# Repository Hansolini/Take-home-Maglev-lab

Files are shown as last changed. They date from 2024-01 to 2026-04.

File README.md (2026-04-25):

# Take-home Maglev lab \:magnet\:

<table align="center">
  <tr>
    <td align="center">
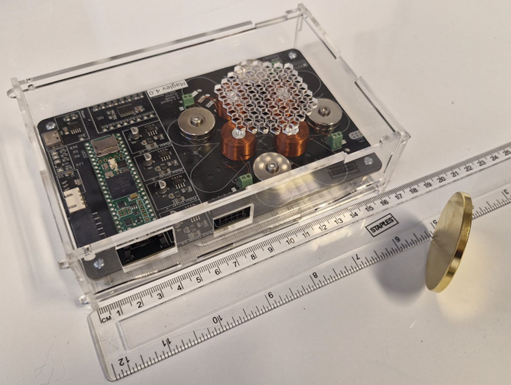
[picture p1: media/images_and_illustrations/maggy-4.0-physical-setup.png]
current hardware
      <br>
      1) Current version of the hardware.
    </td>
    <td align="center">
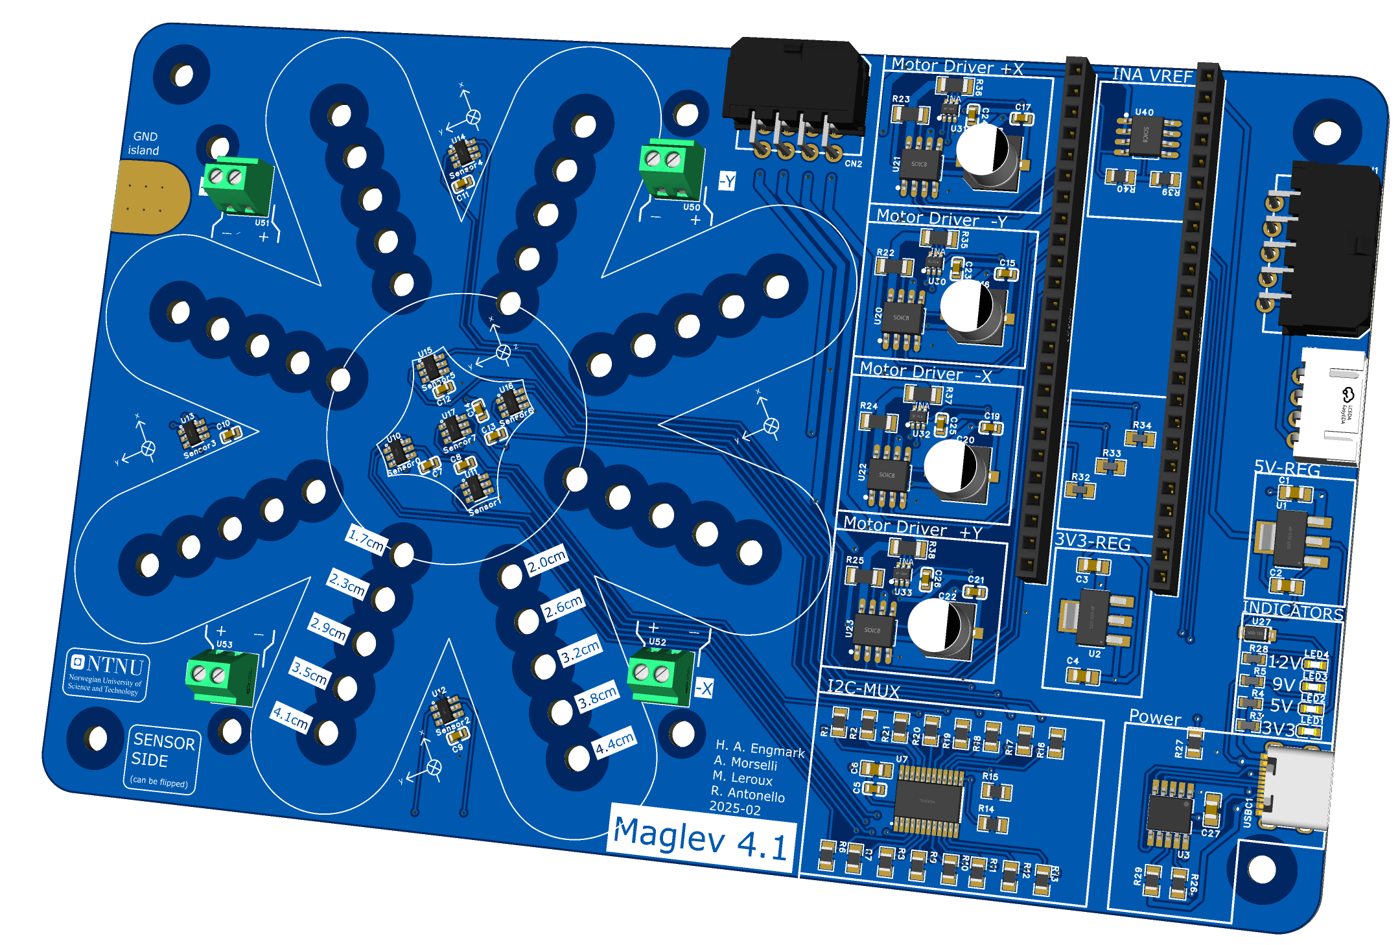
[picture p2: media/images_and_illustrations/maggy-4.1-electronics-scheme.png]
current electronics
      <br>
      2) Overview of the current PCB.
    </td>
    <td align="center">
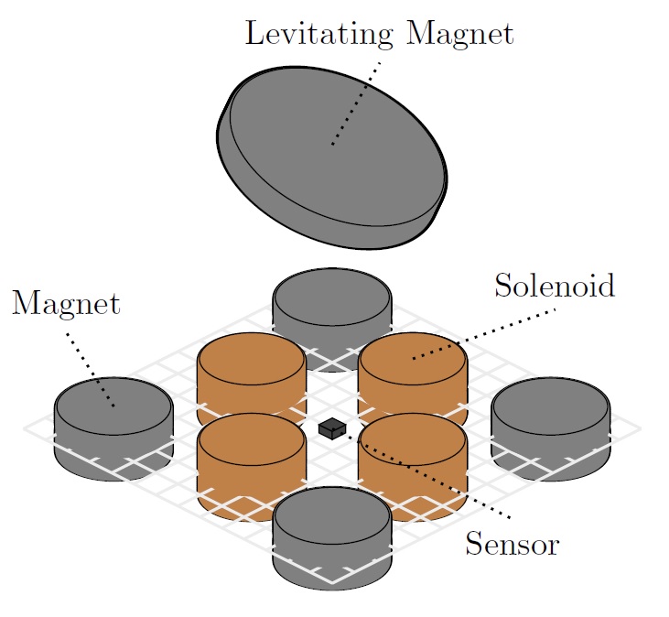
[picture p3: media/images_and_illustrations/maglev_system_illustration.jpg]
magnetic structure
      <br>
      2) Magnetic structure of the system.
    </td>
  </tr>
</table>

The "Take-home Maglev lab" is a small lab in development at the Norwegian University of Science and Technology (NTNU), University of Padova, Italy, and University in Stavanger, Norway. The setup is tailored to help students learn control and related fields, and is intended as a kit that students can bring home and assemble independently, with additional lab assignments for teaching anything from fundamental to advanced concepts within control engineering.

If you want to see how the platform looks like and how effective it is to achieve levitation (actually with a PD controller in this case), see [this](https://youtube.com/shorts/XnbO15yq0vE) and [this](https://youtube.com/shorts/F0SiuVEP2tM) videos.

As for this repository, it contains a
- **[MATLAB simulator](./simulation),** implementing several models with examples. See [main.mlx](./simulation/main.mlx) for a guide on how to use it.
- **[Design files & software](./physical_system),** and thus PCB files, test code, with examples for how to use the physical system.
- **[Student contributions](./student_contributions),** i.e., theses and project reports from the students that have contributed to the project.

The following is a table about such student reports, summarizing also the hardware development history.
## Project reports \:books\:
### 2022
 1. [M. Brønstad, J. O. Deila, J. Dyerskog, and M. Langklopp, "Magnetic levitation system: Design, prototyping and testing of a digital PID-controller", B.S. thesis, ITK, NTNU, Trondheim, 2022.](./student_contributions/literature/2022_NTNU_bachelor_thesis_MJJM.pdf)
 2. [A. Morselli, "Re-design of a magnetic levitation platform: from an early prototype to a working system", B.S. thesis, DDD, UNIPD, Padova, 2022.](./student_contributions/literature/2022_UNIPD_bachelor_thesis_alberto_morselli.pdf)
 3. [A. Nicetto, "State Space Observers and Controllers for a Take-Home Magnetic Levitation System", B.S. thesis, DDD, UNIPD, Padova, 2022.](./student_contributions/literature/2022_UNIPD_bachelor_thesis_andrea_nicetto.pdf)
 4. [F. D. Marchi, "Modeling and Control of a Magnetic Levitation System", B.S. thesis, DDD, UNIPD, Padova, 2022.](./student_contributions/literature/2022_UNIPD_bachelor_thesis_francesco_de_marchi.pdf)
### 2023
1. [H. A. Engmark, K. T. Hoang, "Modeling and Control of a Magnetic Levitation Platform.", presented at the 22nd IFAC World Congress, Yokohama, 2023 pp. 7276-7281. ](./media/literature/maglev_model_description.pdf)
2. [A. Lincetto, "Towards a Pythonic framework for control and analysis of magnetic levitation systems", B.S. thesis, DDD, UNIPD, Padova, 2023.](./student_contributions/literature/2023_UNIPD_bachelor_thesis_alessandro_lincetto.pdf)
3. [G. Piccolin, "considerations on the software and hardware requirements for the implementation of take-home Maglev control labs", B.S. thesis, DDD, UNIPD, Padova, 2023.](./student_contributions/literature/2023_UNIPD_bachelor_thesis_giulio_piccolin.pdf)
4. [S. Graffer, "State estimation of a Maglev system with the Luenberger observer", Project thesis, ITK, NTNU, Trondheim, 2023.](./student_contributions/literature/2023_NTNU_project_thesis_sverre_graffer.pdf)
5. [P. I. D. K. Fosmo, "Control of a magnetic levitation system using feedback linearization", Project thesis, ITK, NTNU, Trondheim, 2023.](./student_contributions/literature/2023_NTNU_project_thesis_pål_fosmo.pdf)
6. [S. A. Senkaya, "A take home portable MagLev lab for learning electronics and control", Project thesis, ITK, NTNU, Trondheim, 2023.](./student_contributions/literature/2023_NTNU_project_thesis_sacit_ali_senkaya.pdf)
### 2024
1. [P. I. D. K. Fosmo, S. A. Senkaya, S. Graffer, H. A. Engmark, D. Varagnolo, "Maggy: Hands-on control learning with a maglev system", M.S. thesis, ITK, NTNU, Trondheim, 2024.](https://ntnuopen.ntnu.no/ntnu-xmlui/handle/11250/3153592)
2. [P. I. D. K. Fosmo, H. A. Engmark, D. Varagnolo, "Maglev Systems for Control Education", Maglev24, Malmö, 2024.](https://bth.diva-portal.org/smash/get/diva2:1918096/FULLTEXT01.pdf)
3. [A. Dal Bello, "Tracking Visual Markers For Maglev Platforms", B.S. thesis, DSMN, UNIVE, Venezia, 2024.](./student_contributions/literature/2024_UNIVE_bachelor_thesis_alessandra_dal_bello.pdf)
4. [G. D'Auria, "Computer based state observers for magnet systems", B.S. thesis, DEI, UNIPD, Padova, 2024.](./student_contributions/literature/2024_UNIPD_bachelor_thesis_giuseppe_d'auria.pdf)
### 2025
1. [Ø. Damsgaard, "Moving horizon state estimation for predictive control of magnetic levitation systems", M.S. thesis, ITK, NTNU, Trondheim, 2025](./student_contributions/literature/2025_MSc_thesis_-_Ørnulf_Damsgaard_-_Moving_horizon_state_estimation_for_predictive_control_of_magnetic_levitation_systems.pdf.pdf)
2. [M. Mjelde, "Robust Model Predictive Control for a Magnetic Levitation System", M.S. thesis, ITK, NTNU, Trondheim, 2025](./student_contributions/literature/2025_MSc_thesis_-_Mikael_Mjelde_-_Robust_Model_Predictive_Control_for_a_Maglev.pdf)
3. [L. Ongaro, "Adapting a maglev system for the ball and beam control", B.S. thesis, University of Padova, 2025](./student_contributions/literature/2025_BSc_thesis_Ongaro_Leonardo_Adapting_a_maglev_system_for_the_ball_and_beam_control.pdf)
4. [M. Palamin, "Comunicazione tra un sistema maglev e dispositivi esterni: implementazione e implicazioni per la didattica sulla Teoria del Controllo", B.S. thesis, University of Padova, 2025](./student_contributions/literature/2025_BSc_thesis_Palamin_Manuel_Comunicazione_tra_un_sistema_maglev_e_dispositivi_esterni.pdf)
5. [T. Chinello, "Bode and Nyquist plots for the analysis and control of a magnetic levitation system", B.S. thesis, University of Padova, 2025](./student_contributions/literature/2025_BSc_thesis_Chinello_Tommaso_Bode_and_Nyquist_plots_for_the_analysis_and_control_of_a_magnetic_levitation_system.pdf)
6. [T. A. Jonsson, "Implementation of a Moving Horizon Estimator Using the Acados Framework", M.S. project, ITK, NTNU, Trondheim, 2025](./student_contributions/literature/2025_Prosjektoppgave_-_Thomas_Aleksander_Jonsson_-_MHE_for_Maggy.pdf)
7. [E. Bruaset, "Acados-based Implementation of Nonlinear MPC for Magnetic Levitation", M.S. project, ITK, NTNU, Trondheim, 2025](./student_contributions/literature/2025_Prosjektoppgave_-_Eivind_Bruaset_-_Acados_for_Maggy.pdf)
8. [L. Edvardsen, "Reinforcement Learning for MagLev Control", M.S. project, ITK, NTNU, Trondheim, 2025](./student_contributions/literature/2025_Prosjektoppgave_-_Linus_Edvardsen_-_RL_for_Maggy.pdf)
9. [M. Jullum Faanes, "CasADi-based Implementation of Nonlinear MPC for Magnetic Levitation", M.S. project, ITK, NTNU, Trondheim, 2025](./student_contributions/literature/2025_Prosjektoppgave_-_Marius_Jullum_Faanes_-_SMPC_for_Maggy.pdf)

## Development history \:rocket\:
| **Version** | **Developer**                                                  | **Goal**                                                      | **Development period** |      **Status**      | **Result**                  |
| ----------- | -------------------------------------------------------------- | ------------------------------------------------------------- | ---------------------- | :------------------: | --------------------------- |
| V1.0        | M. Brønstad <br> J. O. Deila <br> J. Dyrskog <br> M. Langklopp | Levitaion                                                     | Spring 2022            | \:white_check_mark\: | Stable levitation ~ 2 min   |
| V2.0        | M. Brønstad <br> J. O. Deila <br> J. Dyrskog                   | Smaller form factor, more robust                              | Summer 2022            | \:white_check_mark\: | Stable levitation >> 2 min  |
| V2.5        | JH Technical AS                                                | Fix minor bugs, improve heating and components                | Spring 2024            | \:white_check_mark\: | Stable levitation >> 2 min  |
| V2.6        | A. Morselli                                                    | Fix faulty wiring, changing sensors                           | Spring 2024            | \:white_check_mark\: | Stable levitation >> 30 min |
| V2.7        | A. Morselli                                                    | Modular design and testbench for V3.0                         | Spring 2024            | \:white_check_mark\: | Decisions on design         |
| V3.0        | A. Morselli                                                    | Modular redesign for first 'Take-home lab'                    | Summer 2024            | \:white_check_mark\: | Decisions on design         |
| V3.1        | M. Leroux                                                      | Adding USB-C power                                            | Fall 2024              | \:white_check_mark\: | Improved power delivery     |
| V4.0        | M. Leroux                                                      | New form factor and additional sensing for improved stability | Fall 2024              | \:white_check_mark\: | Improved control            |
| V4.1        | R. Antonello                                                   | Rerouting PCB tracks and updating components                  | Spring 2025            | \:white_check_mark\: | Meets IPC standards         |
| V4.2        | K. Blom                                                        | Creating a MISO version of the board                          | Spring 2025            | \:white_check_mark\: | MISO board                  |
| V4.3        | A. Morselli                                                    | Improving EM compatibility via some rerouting                 | Fall 2025              | \:white_check_mark\: | Improved EM compatibility   |

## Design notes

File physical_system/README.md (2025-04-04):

 Here you find:
- **Hardware:** Blueprints for circuit designs of every version of Maggy, components lists and vector files for protective covers/boxes, as well as test-code for checking if the assembeled hardware works as expected.
- **Software:** Various examples of how to use the different veersions of maggy, e.g., PD control embedded on Teensy, and communication protocols for monitoring and control with a computer.

## Setting up for programming Maggy

Each version of Maggy contains a Teensy 4.1 microcontoller, which handles all of the sensor measuremetns, communication and control. This is easily programmed using the Arduino interface, and most of the scripts above are .ino Arduino. To be able to upload these to the Teensy, the following few steps have to be completed:

1.  Install the latest version of [Arduino IDE](https://www.arduino.cc/en/software).

2. When you launch Arduino IDE, you'll see an empty Arduino sketch. Go to **File >> Preferences** (WINDOWS) or **ARDUINO IDE >> Settings** (MAC), and locate the field labeled **"Additional boards manager URLs"** at the bottom of the window, as shown in Figure 1. Paste the following link into the field:
	- [https://www.pjrc.com/teensy/package_teensy_index.json](https://www.pjrc.com/teensy/package_teensy_index.json)
    Use a comma to separate it if there is already something written in the field.

    <td align="center">
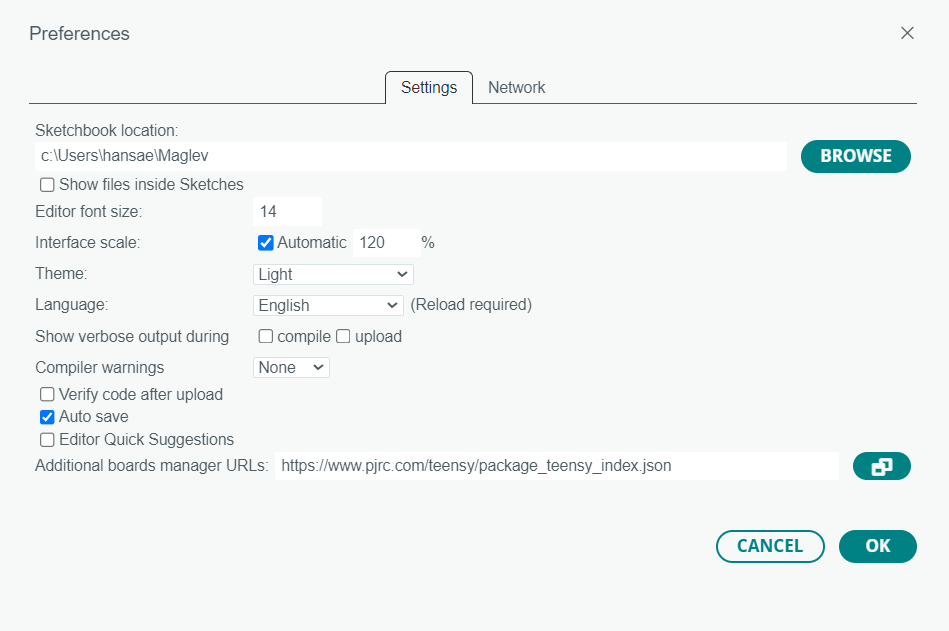
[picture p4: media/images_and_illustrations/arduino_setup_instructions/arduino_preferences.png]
arduino_preferences
      <br>
      Figure 1: Arduino IDE preferences.
    </td>

---

3. Click on **"Boards Manager"** in the toolbar on the left side of the Arduino IDE home screen. Search for "Teensy" and install the Teensy package by Paul Stoffregen, as shown in Figure 2.

	<td align="center">
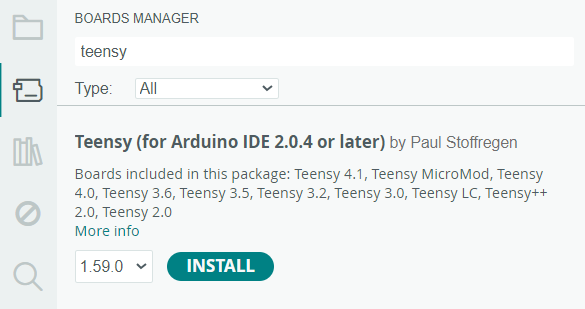
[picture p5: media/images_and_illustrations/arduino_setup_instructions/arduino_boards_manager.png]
arduino_boards_manager
	  <br>
	  Figure 2: Arduino IDE boards manager.
	</td>

---

4. Click on **"Library Manager"** on the left toolbar, search for "TLE493D" (V2x) or "TLV493D" (V4x) in the search field, and install the package from "Infineon Technologies", as shown in Figure 3.

	<td align="center">
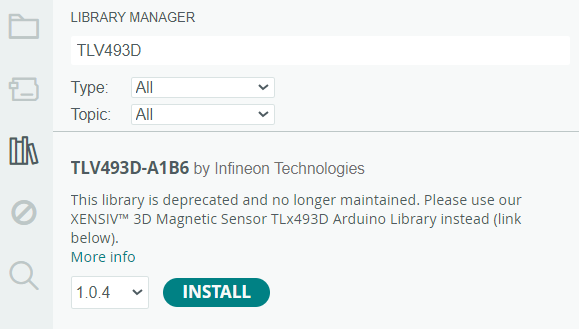
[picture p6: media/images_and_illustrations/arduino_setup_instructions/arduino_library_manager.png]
arduino_library_manager
	  <br>
	  Figure 3: Arduino IDE library manager.
	</td>

---

> **NOTE**: Before powering Maggy, remove the large disk magnet from the system. The scripts we'll run later perform bias-removal routines for measurements, and we don't want to remove the effect of the levitating magnet.

---

5.  Connect Maggy and Teensy to your PC with a micro-USB cable.[1](https://chatgpt.com/c/67e6699f-81f0-8013-9739-4315bfa6288c#user-content-fn-1) Check that you can upload a blank sketch by selecting the COM port of Teensy 4.1 from the **"Select board"** drop-down menu at the top of the window. Click **"Upload"** to compile and upload the sketch to Teensy 4.1. You'll see a lot of red text in the console window during compilation and uploading, but the process is successful if the last lines of text appear as shown in Figure 4.

	<td align="center">
	  teensy_success_message<br>
	  Figure 4: Arduino IDE command window message upon successful compilation.
	</td>
## Footnotes

1. If the Teensy isn't recognized by the PC, connect external power to Maggy by plugging in the power cable on the opposite side of the USB port. [↩](https://chatgpt.com/c/67e6699f-81f0-8013-9739-4315bfa6288c#user-content-fnref-1)

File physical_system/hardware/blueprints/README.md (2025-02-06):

# Blueprints :hammer_and_wrench:
This folder contains information about the hardware for all the different versions of Maggy.

## PCB Designs
The PCB design and production files can be found in each folder. Starting with version 4, it is also possible to view the designs and place orders through EasyEDA. Please refer to the specific folders for more information.

## Other Components
Each version of Maggy uses additional components that must be purchased separately from the PCB files.

### Teensy 4.1
We use the Teensy 4.1 development board, specifically this one:
- [Teensy 4.1 on Elfa Distrelec](https://www.elfadistrelec.no/no/teensy-utviklingskort-med-headers-sparkfun-electronics-dev-16996/p/30216161?ext_cid=shgooaqnono-Shopping-PerformanceMax-CSS&cq_src=google_ads&cq_cmp=20351270785&cq_con=&cq_term=&cq_med=pla&cq_plac=&cq_net=x&cq_pos=&cq_plt=gp&gclid=CjwKCAjw4P6oBhBsEiwAKYVkq0jYkFst_neMMFQlXfZBW9-KxBMFTjGZog-tAYaTsAmTVziUdTWCHRoCGOcQAvD_BwE&gclsrc=aw.ds)
- [Teensy 4.1 on RS Online](https://no.rs-online.com/web/p/microcontroller-development-tools/2836911?cm_mmc=NO-PLA-DS3A-_-google-_-CSS_NO_EN_Pmax_Test-_--_-2836911&matchtype=&&gad_source=1&gclid=CjwKCAiA74G9BhAEEiwA8kNfpfuTP6LMEUCaeJ0THdqRm6JLBaF8OzCmbcy2USRwfd5TNwAT9TSBZxoCiPkQAvD_BwE&gclsrc=aw.ds)

If you want to avoid a lot of soldering, ensure that you order with the headers pre-soldered.

### Electromagnets
The electromagnets are standard 19×12 mm copper coils with around 480 windings. Searching for “19x12 maglev electromagnet” should result in many options. For example:
- [Electromagnet on AliExpress](https://www.aliexpress.com/item/4000076659177.html?spm=a2g0o.productlist.main.1.455ew7Phw7PhcV&algo_pvid=489107c2-cb2e-4235-b999-33f5bcec5149&algo_exp_id=489107c2-cb2e-4235-b999-33f5bcec5149-0&pdp_npi=4%40dis%21EUR%216.78%216.24%21%21%217.18%216.61%21%402103249617062671537431660e604c%2110000015610528766%21sea%21NO%210%21AB&curPageLogUid=W7mtjk8XbjMA&utparam-url=scene%3Asearch%7Cquery_from%3A)
- [Electromagnet on Amazon (US)](https://www.amazon.com/Magnetic-Levitation-Electromagnetic-Induction-Experiment/dp/B0B92X4MB2?th=1)
- [Electromagnet on Amazon (DE)](https://www.amazon.de/-/en/Magnetic-Floating-Electromagnetic-Induction-Experiment/dp/B0B8Z66W5S)

### Permanent Magnets for the Base
For the base, we use neodymium magnets with counterbore holes that are fastened with screws to the PCB. The choice of magnet is flexible, but ensure that the dimensions are similar to the ones listed below. The stronger the magnet, the better (i.e., N40 > N35). Also, all magnets on a single unit should have the same polarity, so it’s advisable to purchase them from the same supplier.

Examples of magnets we have used:
- [20×4 mm Magnet with Mounting Hole (Supermagneter)](https://supermagneter.no//magnet-med-monteringshull-20x4mm-id794)
- [20.0×4.5×4.0 mm Neodymium Ring Magnet (Magnet-Shop)](https://www.magnet-shop.com/neodymium/ringmagnets/ringmagnet-20.0x4.5x4.0-mm-n42-nickel-counterbore-n-pole)

### Disk Magnets
The choice of disk magnets is even more flexible, but the examples below are good options. Thicker and heavier magnets have a higher moment of inertia, which makes them easier to stabilize.
- [50×5 mm Disk Magnet (Supermagneter)](https://supermagneter.no//diskmagnet-50x5mm-id752)
- [50.0×4.0 mm Neodymium Disk Magnet (Magnet-Shop)](https://www.magnet-shop.com/neodymium/discmagnets/discmagnet-50.0-x-4.0-mm-n40-gold-holds-21-kg)

### Misc
Screws, spacers and nuts are all standard 3 mm machine screws that should be available everywhere. If possible, use non-magnetic screws. In particular, we have used these spacers for space between PCB and covers/box:
- [M3 spacer, 15mm, male-female](https://www.digikey.no/no/products/detail/w%C3%BCrth-elektronik/971150354/9488642)
- [M3 spacer, 15mm, female-female](https://www.digikey.no/no/products/detail/w%C3%BCrth-elektronik/970150354/9488567)

Also consider that you might need [USB cables](https://www.digikey.no/no/products/detail/cvilux-usa/DH-20M50057/13177527) for connecting to a computer, some antistatic insulation and cardboard boxes for storage, and laser cut protective plates/boxes for protection (we have used 3 mm acrylic plates, cut with blueprints found in the folders).

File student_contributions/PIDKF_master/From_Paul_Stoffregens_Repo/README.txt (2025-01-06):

This folder contains the code developed by Paul Stoffregen to test Teensy data transmission speed.
I do not claim ownership of any of the code, and credit goes to the original developer.
The original code is located at https://github.com/PaulStoffregen/USB-Serial-Print-Speed-Test/tree/master.

-Pål Ivar Delphin Kværnø Fosmo, June 3rd 2024

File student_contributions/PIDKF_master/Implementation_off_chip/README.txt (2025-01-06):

This folder contains code related to the off-chip implementation described under "Implementation study: off-chip computations" in Chapter 15 - Controller implementation.

"Transmission_Speed_Test" includes the code for testing general data transmission time between Teensy and MATLAB. Start the Teensy code first, and then the MATLAB
script shortly thereafter. Follow method outlined in thesis.

"Data_sending_test_final" includes the code used for testing the transmission time when meaningful data was actually transmitted, that is the
test outlined where Teensy generates 10 random states and MATLAB calculates input based on them and send it back to the Teensy.
The code is divided into Arduino code for the Teensy and MATLAB code for running on a computer.
To conduct a test, start running the Teensy code "Data_sending_test_final.ino", and wait for a couple of seconds before running the MATLAB script.

The results should arrive within a couple of seconds. The MATLAB script is also equipped with plotting of some of the results. The plot where
this implementation approach is compared to the on-chip approach also includes data from .csv-files. This data is collected from the on-chip
implementation direction.

-Pål Ivar Delphin Kværnø Fosmo, May 27th 2024

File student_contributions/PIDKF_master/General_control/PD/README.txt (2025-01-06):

This folder contains code related to the PD controller described under "General control" in Chapter 14 - Stabilizing the system.
The code is a stand-alone Arduino sketch for direct implementation of said controller on the Teensy, more or less "plug-and-play". Developed
by Hans Alvar Engmark and Sverre Graffer.

-Pål Ivar Delphin Kværnø Fosmo, May 27th 2024

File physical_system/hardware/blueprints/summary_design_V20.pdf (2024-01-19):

# Maglev summer project - note

Martin Brønstad, Jørn Deila, Jørgen Dyrskog

martin.bronstad@ntnu.no, jodeila@stud.ntnu.no, jorgen.dyrskog@ntnu.no

June 2023

## 1 Introduction

This note is meant to document some of the simulation and modelling work done during our maglev summer project. See the model description paper for more details on the system model. Model description and simulation framework were provided by Hans A. Engmark, hans.a.engmark@ntnu.no.

## 2 Modelling

We wanted to confirm the assumed polarization of the magnets of J = 1.22. To do this we measured the flux produced by each magnet with a hall effect sensor. The polarization J were then found by inserting I = Kl in equation 1b in the model description and solving for K.

### 2.1 Permanent magnets

Measured flux B = 0.064T with sensor in position s =

h

0 0 0.025iT
relative to the magnet center. These values yield J = 1.1, which seemed reasonable for a magnet of grade N35. The measurements also corresponded well with results from magnetic field calculators.

### 2.2 Levitating manget

Measured flux B = 0.0544T with sensor in position s =

h

0 0 0.0125iT
relative to the magnet center. These values yield J = 0.8. This is quite a bit lower than expected. The field strengt should have been about 0.09T according to a magnetic field calculator (assuming a magnet grade of N38). Several measurements with different sensors yielded the same result. The measured value was used in simulations and the designed system should work for the current levitating magnet, but the discrepancy in values might be useful to keep in mind should one wish to replace the levitating magnet in the future.

### 2.3 Solenoids

We opted to model and use the solenoids from the analog system. The flux were measured while applying

a current to one solenoid. Sensor were placed in s =

h

0 0 0.005iT
relative to the solenoid center. With I = 0.9A, B = 0.0448T. With I = 1.5A, B = 0.0640T. Simulation of the same conditions yielded B = 0.0226T and B = 0.0377T respectively. This is most likely caused by the solenoids having a relative permeability µ > 1. Our solution was to increase the number of windings to 1050, which seemingly made the simulations behave more accurately in our use case. This might not be the best solution for more extensive simulation and model based control however, and should perhaps be looked further into in the future.

1

## 3 Simulations

The provided simulation framework was used to look at different configurations of the system, and used in combination with electrical design and other practical considerations to decide the final setup. This section covers the parameters and simulation results of the final system setup.

### 3.1 Parameters

Permanent magnets

x[m] | 0 √.004
| 2

h

| 1 −1 −1 1i
y[m] | 0 √.004
| 2

h
| 1 1 −1 −1

i

z[m] | l
| 2

h

| 1 1 1 1i
l[m] | 0.01
r[m] | 0.01
J[T] | 1.1
| Levitating magnet
m[kg] | 0.075
l[m] | 0.005
r[m] | 0.025
J[T] | -0.8
| Solenoids
x[m] | 0.02 h 1 0 −1 0i
y[m] | 0.02 h 0 1 0 −1

i

z[m] | l
| 2

h

| 1 1 1 1i
l[m] | 0.02
r[m] | 0.01
nw | 1050

Table 1: Simulation parameters

### 3.2 Z-graph

The system in its unforced state will have a z-graph as shown in figure 1. The vertical equilibrium point

is then in ηeq =

h

0 0 0.037iT

### 3.3 Solenoids

As a measure of the solenoids ability to influence the position of the levitating magnet the force in x-direction was plotted as shown in figure 2. The levitating magnet is moved along the x-axis with a height equal to the vertical equilibrium. The blue plot shows the unforced system, and red shows the case

where u =

h

−0.8 0 0.8 0iT
. Depending on the control structure, the solenoids at max actuation should in theory be able to stabilize the magnet within x = ±0.006 of the origin at zeq = 0.037.

2

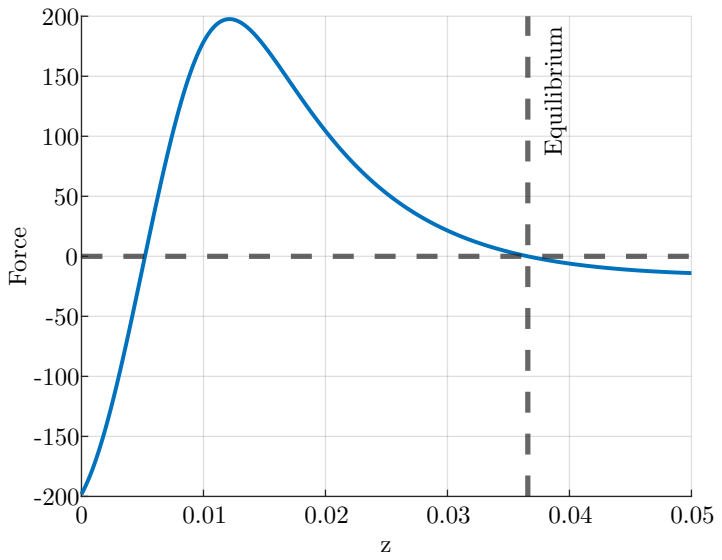
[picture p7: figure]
Force; Equilibrium

Figure 1: Forces on levitating magnet in z-direction.

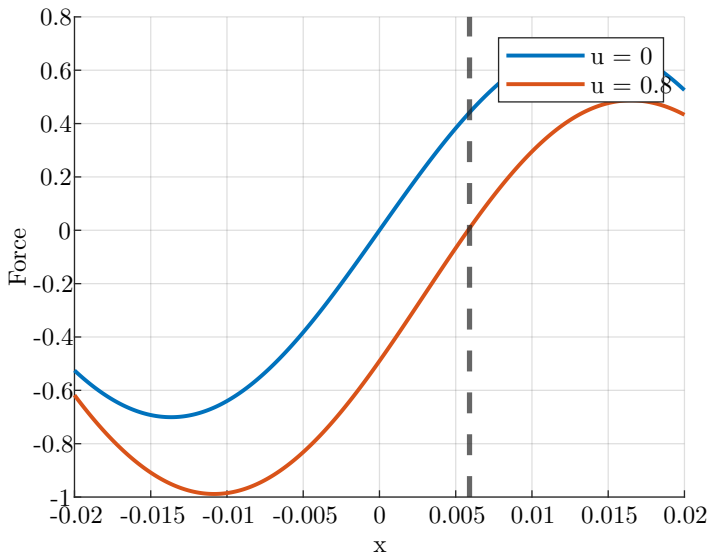
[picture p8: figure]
Force

Figure 2: Forces on levitating magnet in x-direction with and without solenoid actuation.

### 3.4 Sensor placement

In addition to the 3-axis hall effect sensor in the middle of the platform, we wanted the opportunity to place two other 3-axis sensors off-center to improve the observability of the system. It is desirable to put these sensors in positions where the changing magnetic field of the solenoids cancel out to minimize the measurement disturbance. Given a control structure where opposing solenoids use inverted currents, that is u =

h
ux | uy | −ux | −uy

i
. These positions were found to be in x = ±0.0186, y = ±0.0186, as shown in figure 3.

3

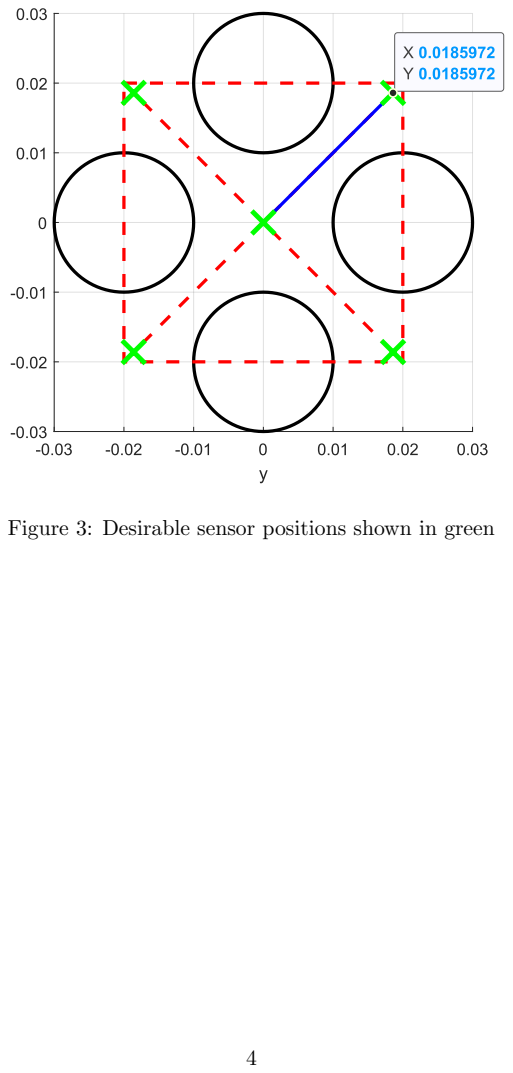
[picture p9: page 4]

Figure 3: Desirable sensor positions shown in green

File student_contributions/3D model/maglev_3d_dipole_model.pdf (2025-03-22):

# Dipole Model of Maggy

H.A.E

March 22, 2025

## 1 Introduction

TODO: Add some illustration and explanation of the system/model here.

## 2 Nomenclature

Position and Geometry

ri | Position of magnet i in the base [m]
rj | Position of sensor j in the base [m]
r | Position of levitating magnet [m]
di := r − ri | Vector from magnet i to levitating magnet [m]
di := ∥di∥ | Distance from magnet i to levitating magnet [m]
dj := rj − r | Vector from levitating magnet to sensor j [m]
dj := ∥dj∥ | Distance from levitating magnet to sensor j [m]

Orientation and Motion

η := [ϕ, θ, ψ]

T | Euler angles (ZYX convention) [rad]
ω | Angular velocity of levitating magnet [rad/s]
v | Linear velocity of levitating magnet [m/s]
T | Euler angle rate matrix (ZYX) [−]
R | Rotation matrix (ZYX) [−]

Magnetic Properties

mi | Magnitude of magnetic moment in base magnet i [A · m² ]
m | Magnitude of levitating magnet’s magnetic moment [A · m²
]
mi := [0, 0, mi]

T Magnetic moment vector of base magnet i [A · m² ]

m := R[0, 0, m]

T | Magnetic moment vector of levitating magnet [A · m² ]
µ0 | Magnetic permeability of free space (4π · 10⁻⁷ ) [H/m]
Bj | Magnetic field at sensor j [T]

System Parameters

M | Mass of the levitating magnet [kg]
I | Inertia matrix of the levitating magnet [kg · m² ]
g | Gravitational acceleration constant [m/s² ]

g := [0, 0, −g]

T | Gravity vector [m/s² ]
Ii | Current in solenoid i [A]
nw | Number of windings per solenoid [−]

States and Dimensions

x | State vector [mixed units]
y | Output/measurement vector [T]
ny | Number of sensors [−]
nu | Number of solenoids/magnets in the base [−]

## 3 Equations

### 3.1 Rotational matrices

R =

cos ψ cos θ cos ψ sin θ sin ϕ − sin ψ cos ϕ cos ψ sin θ cos ϕ + sin ψ sin ϕ sin ψ cos θ sin ψ sin θ sin ϕ + cos ψ cos ϕ sin ψ sin θ cos ϕ − cos ψ sin ϕ
− sin θ | cos θ sin ϕ | cos θ cos ϕ

, | (1a)

T =

1 sin ϕ tan θ cos ϕ tan θ
0 | cos ϕ | − sin ϕ
0 | sin ϕ cosθ | cos ϕ cosθ

. | (1b)

### 3.2 Magnetic field

The magnetic field measured in sensor j from the levitating magnet is

Bj =

µ0
4πd³
j

"
3

(m · dj)dj
d

2
j

− m

. | (2)

### 3.3 Force and torque

The magnetic force and torque from magnet i acting on the levitating magnet are

Fi =

3µ0
4πd⁵
i
(mi · di) m + (m · di) mi + (mi · m) di −

5 (mi · di) (m · di)
d

2
i

di

, | (3a)

τi =

µ0
4πd³
i
m ×
3 (mi · di) di
d

2
i

− mi

. | (3b)

### 3.4 Equations of motion

The motion of the levitating magnet is described by

Mv˙ =

# Xnu

i=1

Fi + Mg, | (4a)

Iω˙ =

# Xnu

i=1

τi − ω × (Iω). | (4b)

## 4 Complete state-space model

x˙ =

v

T

−1ω

1
M (

# Pnu

i=1 Fi + Mg)

I

−1
(

# Pnu

i=1

τi − ω × (Iω))

, | (5a)

y =

B1
Bny

. | (5b)

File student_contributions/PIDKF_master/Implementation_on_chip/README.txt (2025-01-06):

This folder contains code related to the off-chip implementation described under "Implementation study: embedded computations" in Chapter 15 - Controller implementation.

All code is included for a direct run of the controller on the Teensy. Included is also a test scheme for the controller to time its performance.
Ten states are generated at random and fed through the code and timed. The times are then written to the serial monitor for saving to a .csv-file
or something.

-Pål Ivar Delphin Kværnø Fosmo, May 27th 2024

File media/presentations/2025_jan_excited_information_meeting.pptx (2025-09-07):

## Magnetic Minds: An Interactive Learning Platform for Maglev Labs

NTNU

ITK

31.01.25

Purpose
  - Enhancing the value of take-home maglev labs previously funded by Excited by means of adaptive dynamic learning platform
Team
  - Hans Alvar Engmark and Morten Dinhoff Pedersen (ITK)
  - Lasse Mostad (ILU)
  - 6 computer science students (IDI)
Implementation roadmap
  - Feb. to March Mapping out requirements and explore options
  - April to June Development and internal tests of the platform
  - July to August Finalization and preparation for assessment
  - Sept. to Dec. Field testing, collecting feedback data
Outcomes
  - A viable prototype for testing
  - Dissemination report from testing phase
  - Publications at conferences and informal workshop at NTNU
Expected impact
  - Assess its usefulness for improving engagement for students
  - Adoption for use with the take-home lab in courses at ITK
  - Extensions to other take-home labs

Levitating
magnet

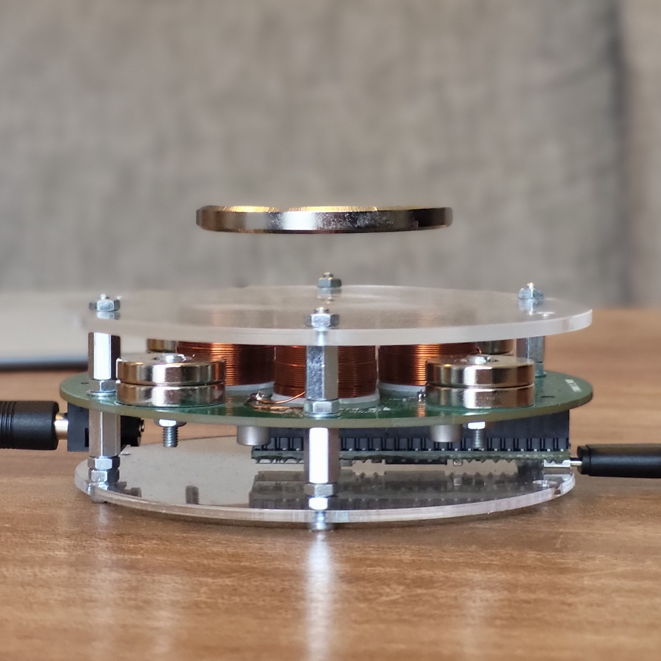
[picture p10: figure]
Et bilde som inneholder innendørs, platespiller, gulv, musikk Automatisk generert beskrivelse

A maglev lab

Microcontroller
programmed
by students

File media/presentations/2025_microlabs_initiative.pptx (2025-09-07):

## Μicrolabs initiative

Lab experiences for everyone – “Kunnskap for en bedre verden”
- Freely available
- Usable everywhere
- Diverse and inclusive community
- Collaborative development

Ambition

Vision

Open sourced microlabs
- Hardware platforms
- Software packages
- Teaching material for instructors and students

Decentralized learning
- Adaptive textbooks
- Assisted self guidance & hybrid learning
- Education research

Infrastructure & administration
- Initially hosted by NTNU
- Independent unit in the future?

Outreach & dissemination
- Workshops
- Publishing
- Development of partnerships

Concept dev. & oversight
- Define what a contribution should look like
- Assessment of contributions

Foundation

Funding

IFAC

Excited 1

Excited 2

NTNU

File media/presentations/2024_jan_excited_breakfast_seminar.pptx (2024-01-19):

## Take-Home Maglev Labs to Promote Self-Efficacy

Topic
  - Development and assessment of a new type of personal lab for engineering students
Team
  - ITK Trondheim
    - Hans Alvar Engmark
    - Morten Dinhoff Pedersen
    - 3 MSc students
  - ITK Ålesund
    - Robin T. Bye et al.
  - External
    - Alberto Morselli, UNIPD, Padova, Italy
Implementation roadmap
  - January – June: Design and build a system, produce learning material
and deploy simple levitation control algorithms
  - June - July: Design our assessment method
(surveys, behavioral observation, interviews, etc.)
  - August: Execute a 2-day mini-course for students at IE
  - Aug. – Sept.: Analyze and disseminate results
Outcomes
  - Working system & teaching material
  - Workshop & dissemination report
  - Papers (Planned for IBCE24, others to be decided)
Expected impact
  - Assess its usefulness as a tool for improving self-efficacy among students
  - Adoption for use in ITK and other departments, and other universities
  - Pave the way for more labs built on the same principle

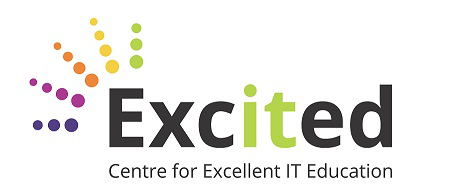
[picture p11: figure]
NTNU Home
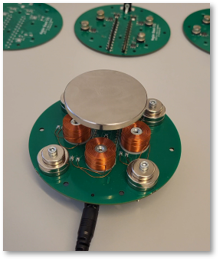
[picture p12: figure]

V2.0 with digital controller

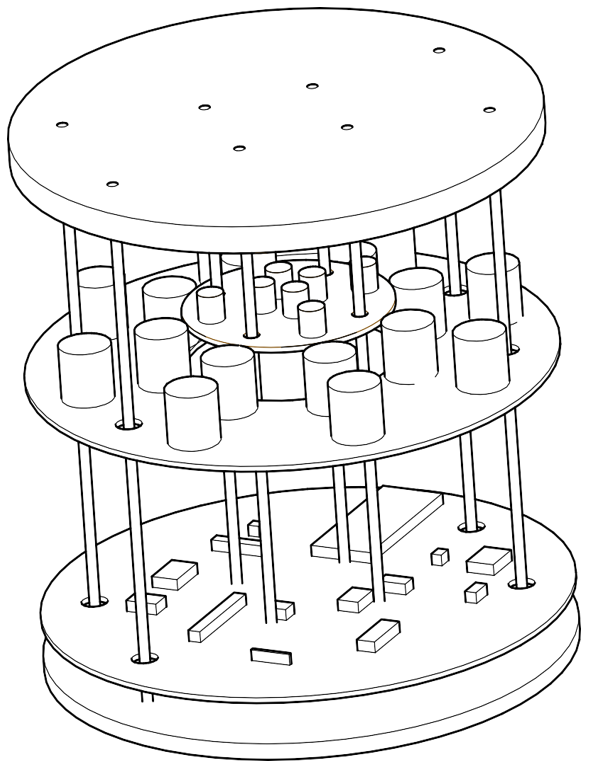
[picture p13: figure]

Illustration of V3.0, courtesy Alberto Morselli

Kunnskap for ei betre verd

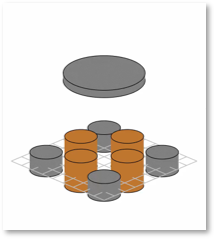
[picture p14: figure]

Simulation with perturbation

Date: 19.01.2024

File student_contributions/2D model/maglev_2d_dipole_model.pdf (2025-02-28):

# 2D Dipole Model of Maggy

H.A.E

February 28, 2025

## 1 Introduction

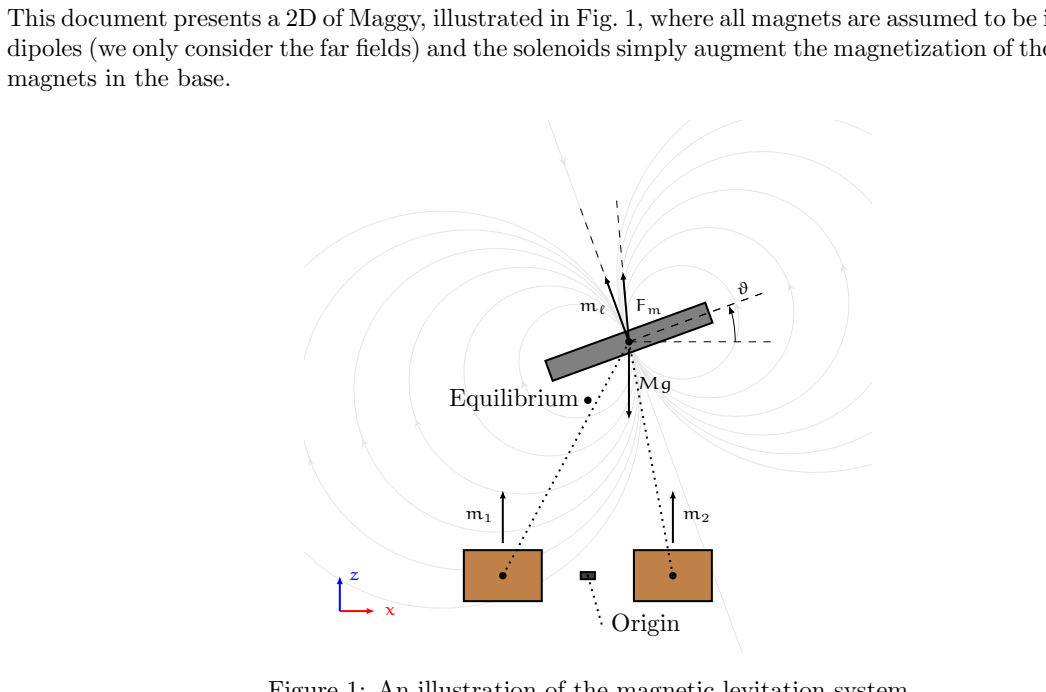
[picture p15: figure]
magnets in the base.; Origin; Equilibrium

This document presents a 2D of Maggy, illustrated in Fig. 1, where all magnets are assumed to be infinitesimal dipoles (we only consider the far fields) and the solenoids simply augment the magnetization of the permanent

Figure 1: An illustration of the magnetic levitation system.

The levitating magnet, with mass M and moment of inertia J, is characterized by the dipole moment

mℓ = mℓ

− sin ϑ
cos ϑ
,

where mℓ := ∥mℓ∥. Each solenoid, located at (xs,i, zs,i) for i = 1, 2, has an effective dipole moment

mi = mi,nom + kIi, k = nwπr² s,i ,

with Ii representing the current in solenoid i. The total magnetic scalar potential, obtained by summing the contributions from both solenoids, governs the magnetic field that exerts force and torque on the levitating magnet. The state of the system is described by

x =

x z ϑ x˙ z˙ ϑ˙

T
| ,

with x and z the position and ϑ the orientation.

## 2 Magnetic Field and Scalar Potential

For solenoid i, the magnetic scalar potential is

ψi =

mi(z − zs,i)
4π [(x − xs,i)

2 + (z − zs,i)

2]

3/2

, | (1)

and the total potential is
ψtot = ψ1 + ψ2. | (2)

The resulting magnetic field is obtained by

B = −µ0∇ψtot = −µ0

∂ψtot
∂x ∂ψtot

∂z

- . | (3)

## 3 Force, Torque, and System Dynamics

The magnetic force acting on the levitating magnet, derived from the gradient of the dot product mℓ · B, is

Fm = mℓµ0∇

∂ψtot
∂x sin ϑ −

∂ψtot
∂z cos ϑ

= mℓµ0

∂

2ψtot
∂x²

sin ϑ −

∂

2ψtot
∂x∂z cos ϑ

∂

2ψtot
∂x∂z sin ϑ −

∂

2ψtot
∂z²

cos ϑ

- . | (4)

The corresponding torque is

τm = mℓµ0

sin ϑ

∂ψtot
∂z + cos ϑ

∂ψtot

∂x
. | (5)

Using Newton-Euler’s equations of motion, the dynamics of the levitating magnet are described by

x¨ =

mℓµ0
M
∂

2ψtot
∂x²

sin ϑ −

∂

2ψtot
∂x∂z cos ϑ
, | (6a)

z¨ =

mℓµ0
M
∂

2ψtot
∂x∂z sin ϑ −

∂

2ψtot
∂z²

cos ϑ

− g, | (6b)

ϑ¨ =

mℓµ0
J
sin ϑ

∂ψtot
∂z + cos ϑ

∂ψtot

∂x
. | (6c)

## 4 Scalar Potential Derivatives

For solenoid i, the first derivatives of the scalar potential are

∂ψi
∂x = −

3 mi(x − xs,i)(z − zs,i)
4π [(x − xs,i)

2 + (z − zs,i)

2]

5/2

, | (7a)

∂ψi
∂z =

mi
4π

"
1
[(x − xs,i)

2 + (z − zs,i)

2]

3/2

− 3

(z − zs,i)

2

[(x − xs,i)

2 + (z − zs,i)

2]

5/2

. | (7b)

The mixed and second derivatives are

∂

2ψi
∂x∂z = −

3 mi(x − xs,i)
4π

"
1
[(x − xs,i)

2 + (z − zs,i)

2]

5/2

− 5

(z − zs,i)

2

[(x − xs,i)

2 + (z − zs,i)

2]

7/2

, (8a)

∂

2ψi
∂x²

= −

3 mi(z − zs,i)
4π

"
1
[(x − xs,i)

2 + (z − zs,i)

2]

5/2

− 5

(x − xs,i)

2

[(x − xs,i)

2 + (z − zs,i)

2]

7/2

, (8b)

∂

2ψi
∂z²

= −

3 mi(z − zs,i)
4π

"
3
[(x − xs,i)

2 + (z − zs,i)

2]

5/2

− 5

(z − zs,i)

2

[(x − xs,i)

2 + (z − zs,i)

2]

7/2

. (8c)

Since ψtot = ψ1 + ψ2, its derivatives are the sums of the corresponding expressions for i = 1 and 2.

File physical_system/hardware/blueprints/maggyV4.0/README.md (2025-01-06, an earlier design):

# Maggy 4.0  

## Hardware Description  

### Table of Contents  

- [Purpose](#purpose)  
- [Teensy](#teensy)  
- [Sensors](#sensors)  
- [Motor Drivers](#motor-drivers)  
- [Solenoids](#solenoids)  
- [Power Supply](#power-supply)  
- [Current Measurement](#current-measurement)  
- [Connectors](#connectors)  
- [Things to Do for V4.1](#things-to-do-for-maggy-4_1)  

## Purpose   

The **Maggy 4.0** represents the latest and most advanced version of the Maggy series, offering substantial improvements over earlier iterations. The new **rectangular design** replaces the previous cylindrical shape to resolve challenges related to design complexity, IPC standards compliance, production risks, and repairability.  

This redesign ensures optimal component arrangement, simplifying both manufacturing and maintenance. It also allows greater flexibility for positioning solenoids and magnets on either side of the board.  

### Key Features Introduced Since Version 2.6:  

- **USB-C power supply**  
- **8 sensors with I2C multiplexer for management**  
- **Terminal blocks for solenoid connections**  
- **Current measurement on solenoids**  
- **Analog I/O signal connector**  
- **External solenoid power connector**  
- **I2C communication for the Teensy**  

These features and improvements will be detailed in the sections below.  

You can join the project on EasyEDA to explore the board design:  
<https://u.easyeda.com/join?type=project&key=e1d90298173405562d58ddb29952aff6&inviter=5f96ec8310644096bd58132cfb3f9c97>  

<p align="center">  
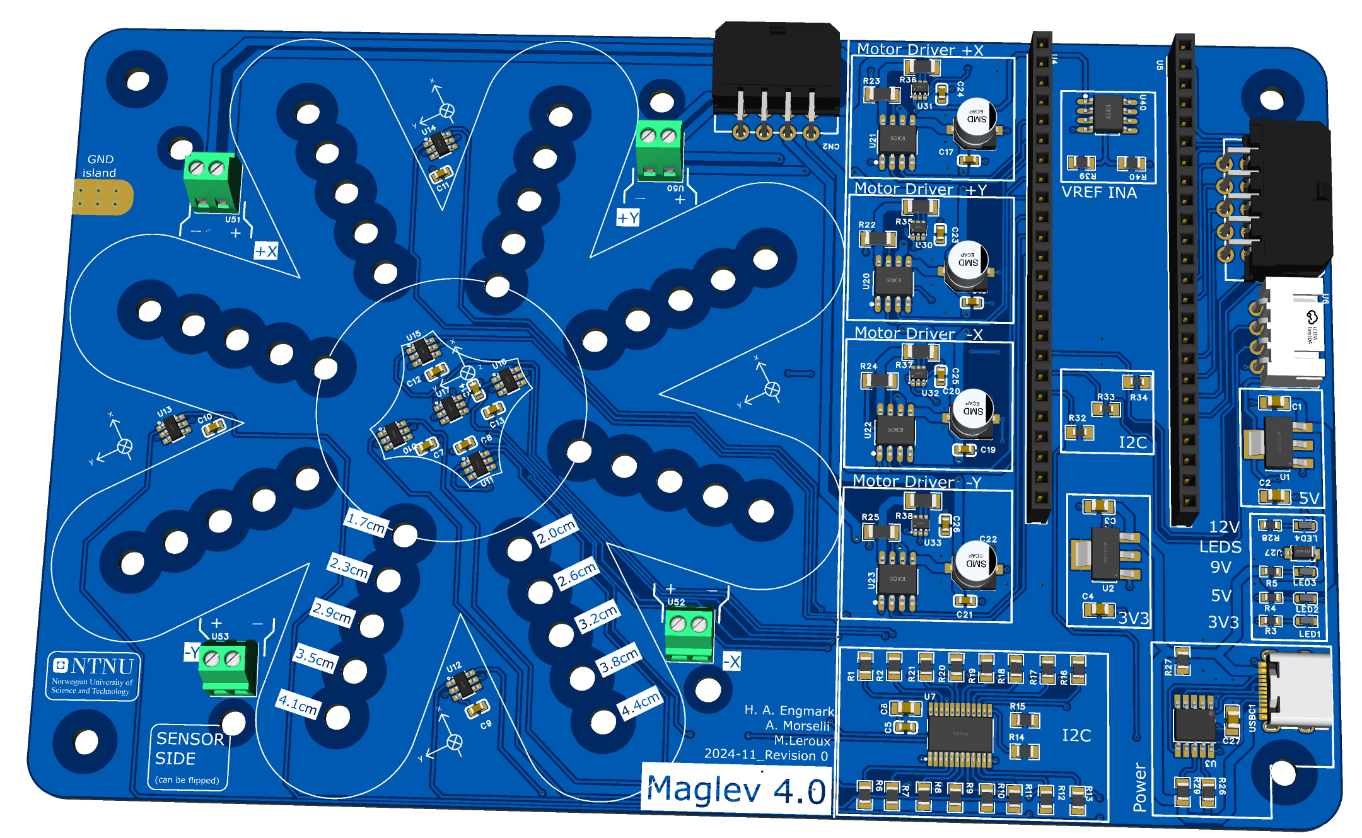
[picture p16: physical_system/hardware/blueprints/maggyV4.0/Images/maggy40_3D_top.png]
Maggy4.0 Top Side
    
  <br><em>Figure 1: Maggy 4.0 Top Side</em>  
</p>  

<p align="center">  
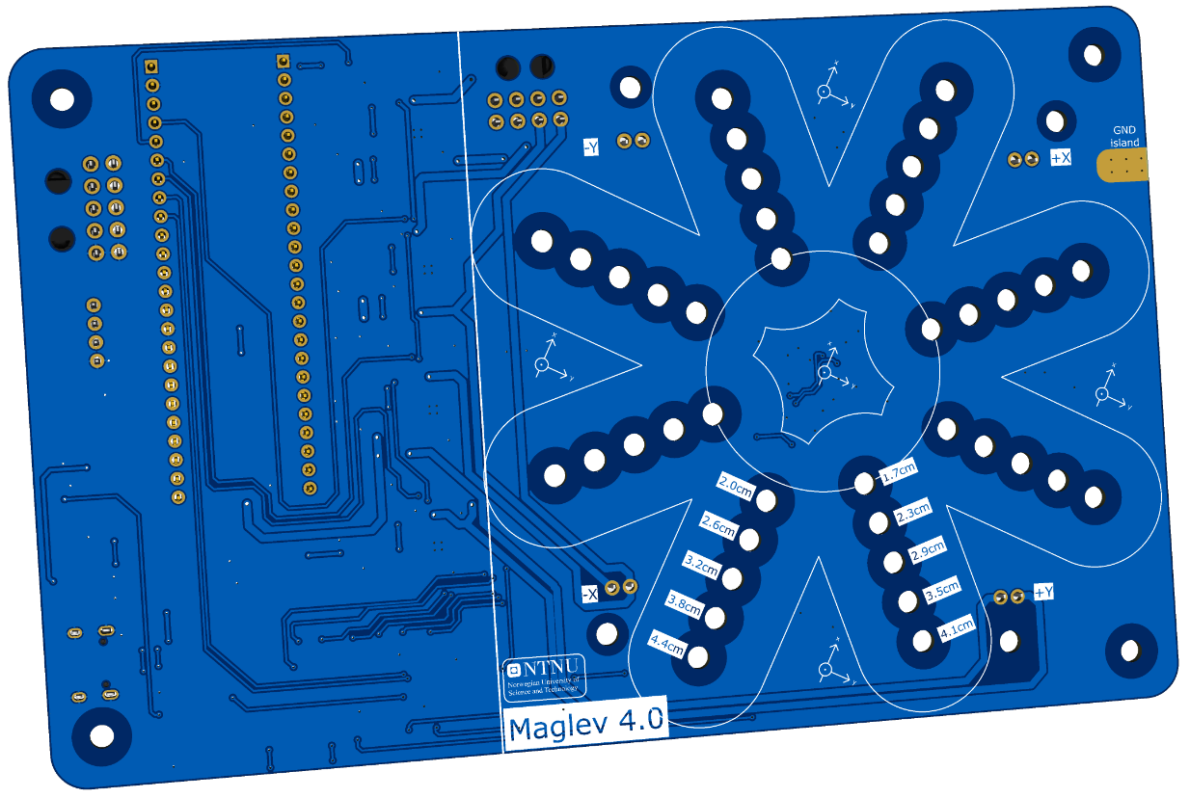
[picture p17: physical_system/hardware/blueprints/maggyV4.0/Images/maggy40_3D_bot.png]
Maggy4.0 Bottom Side
    
  <br><em>Figure 2: Maggy 4.0 Bottom Side</em>  
</p> 

## Teensy

The **Teensy 4.1** microcontroller powers Maggy 4.0, offering high performance and Arduino compatibility. It enables precise magnet levitation control via **I2C communication** with sensors and drives motor controllers for the solenoids.  

With numerous I/O pins, the Teensy can manage current measurements, process analog signals, and integrate external devices, making it highly versatile for advanced projects.  

<p align="center">  
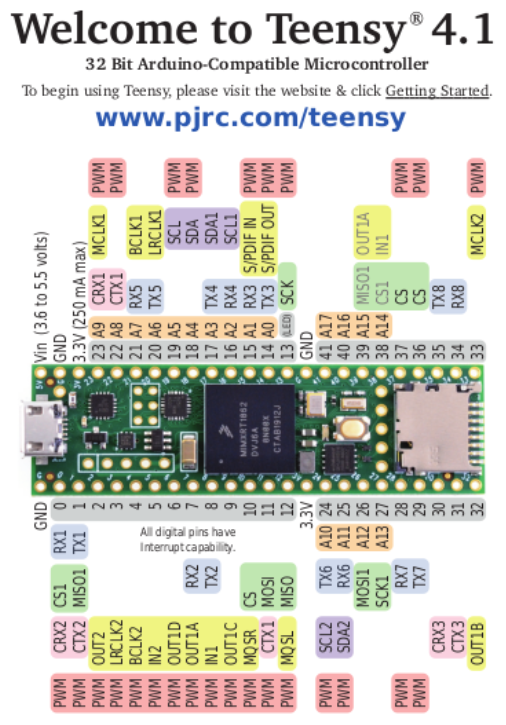
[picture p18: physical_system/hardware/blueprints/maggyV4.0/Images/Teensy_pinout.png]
Teensy Pinout Diagram
    
  <br><em>Figure 3: Teensy 4.1 Pinout Diagram</em>  
</p>  

<p align="center">  
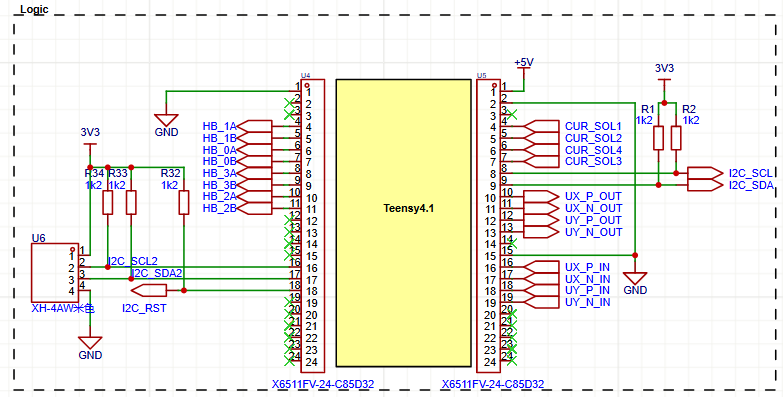
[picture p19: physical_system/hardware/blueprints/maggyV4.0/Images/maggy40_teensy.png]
Teensy on Maggy4.0
    
  <br><em>Figure 4: Teensy 4.1 Mounted on Maggy 4.0</em>  
</p>  

## Sensors

Previous versions used TLE493D Hall effect sensors. However, due to I2C addressing limitations, we 
chose to equip the Maggy 4.0 with eight **TLV493D Hall effect sensors** from Infineon. Although these 
sensors all share the same I2C address, they are individually managed through an **I2C TCA9548 
multiplexer**, which allows each sensor to be selected independently. 

The TLV493D sensors measure the position and strength of a magnetic field by providing values for the 
X, Y, and Z axes. The current code already enables the levitation of a magnet using a central sensor that 
provides the magnet's position. However, the addition of these extra sensors expands the possibilities 
for magnetic field detection on the board, paving the way for advanced measurement and control 
applications.   

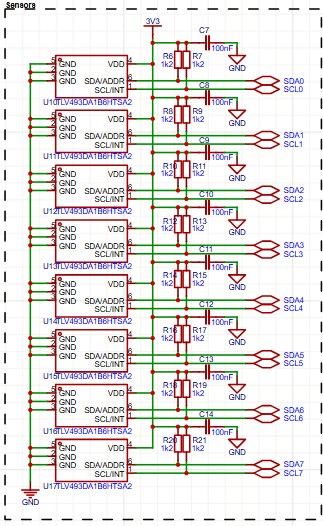
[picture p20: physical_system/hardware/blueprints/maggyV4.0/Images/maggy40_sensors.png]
Sensors on Maggy4.0
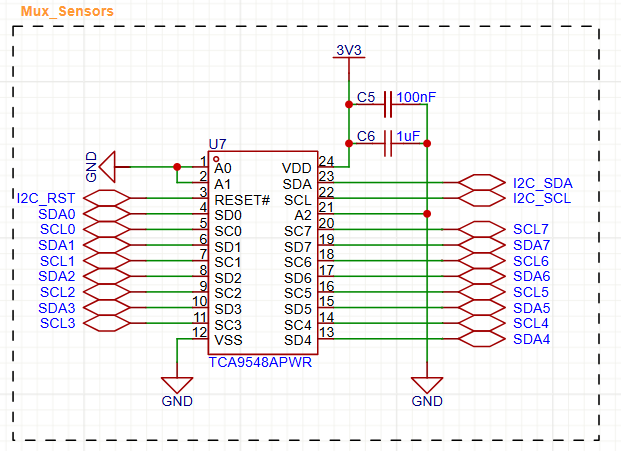
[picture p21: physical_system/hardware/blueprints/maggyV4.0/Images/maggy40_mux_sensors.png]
I2C Multiplexer
|  |  |  
|:-------------------------------------------:|:------------------------------------------:|  
| _Figure 5: Sensors on Maggy 4.0_            | _Figure 6: I2C Multiplexer_                |  

## Motor Drivers 

The Maggy 4.0 is equipped with four **A950 motor drivers**, each capable of independently powering the 
solenoids based on a PWM signal sent by the microcontroller. It is important to note that on the LLS 
pin, there is a resistor whose value determines the current limitation through the solenoids. You can 
adjust this value depending on the desired current. In our case, we limited the current to 1.1 A per 
solenoid. The formula for calculating the appropriate resistor value can be found in the component's 
datasheet. 

<p align="center">  
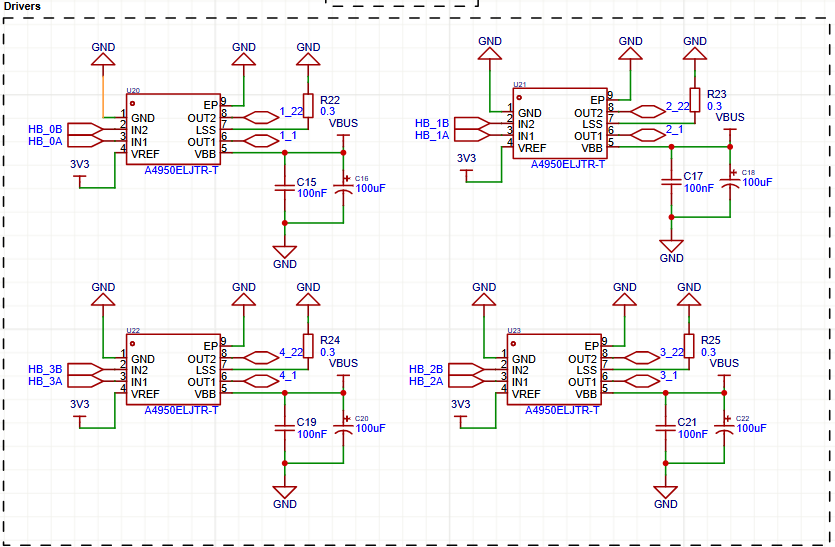
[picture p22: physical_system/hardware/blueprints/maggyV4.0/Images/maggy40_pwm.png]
Motor Drivers Schematic
    
  <br><em>Figure 7: Motor Drivers on Maggy 4.0</em>  
</p>  

## Solenoids

As in previous versions, we use 18.5 mm diameter solenoids with 480 turns and a resistance of 4 ohms. 
When powered, these solenoids generate a magnetic field directed along the Z or -Z axis, depending 
on the current direction. Due to their low resistance, these coils can heat up significantly when used 
for extended periods. Future work could involve resizing the coils by finding larger ones or those with 
higher resistance, while ensuring a balance to avoid compromising the levitation quality. 
The solenoids can be placed on both sides of the board and are connected to the board via terminal 
blocks located on the top side. 

<p align="center">  
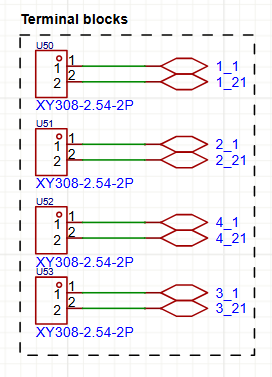
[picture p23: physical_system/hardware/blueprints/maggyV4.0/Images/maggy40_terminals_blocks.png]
Terminal Blocks
    
  <br><em>Figure 8: Solenoid Terminal Blocks on Maggy 4.0</em>  
</p>  

## Power Supply   

In its previous versions, the Maggy was powered by a specific 12V power supply. To make the Maggy 
more flexible and reduce costs by avoiding the need for a dedicated charger, we replaced the Jack 
connector with a **USB-C connector**. However, a simple USB-C connector powers the board with 5V by 
default, which is not sufficient for our use. Therefore, we opted for the Power Delivery (PD) protocol, 
which allows communication with all fast chargers. 

To achieve this, we use the **CH224K integrated circuit**, which manages the Power Delivery 
communication. Its use is simplified by the ability to select the voltage in hardware in several ways (for 
more details, refer to the datasheet). In our case, we chose the simplest solution: a 24kΩ resistor is 
placed on the CFG1 pin, which fixes the voltage to 12V. If the 12V is successfully negotiated, the 12V 
LED will light up. 

Please note that to make this work, you need to power the board with a Power Delivery charger, which 
corresponds to most modern fast chargers and laptop chargers. If your charger cannot provide 12V, the 
integrated circuit will negotiate the highest possible voltage lower than 12V that the charger can supply. 
In many cases, this will be 9V, which is a common voltage for smartphone charging. 

<p align="center">  
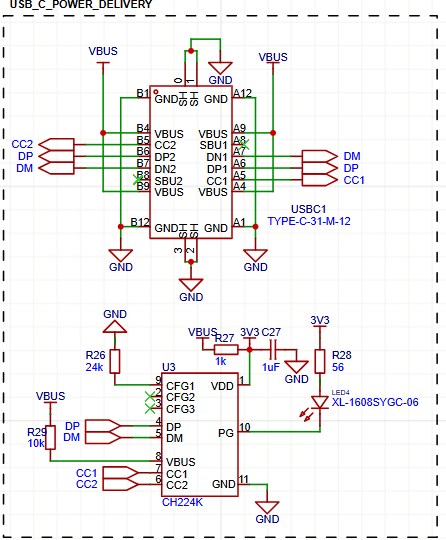
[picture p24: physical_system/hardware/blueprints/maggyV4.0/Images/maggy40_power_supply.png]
Maggy Power Supply Schematic
    
  <br><em>Figure 9: Maggy 4.0 Power Supply Schematic</em>  
</p>  

<p align="center">  
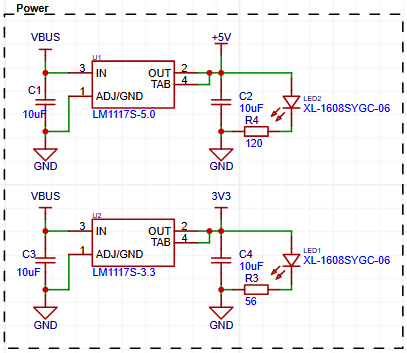
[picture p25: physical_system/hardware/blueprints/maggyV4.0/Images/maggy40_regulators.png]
Maggy Regulators Schematic
    
  <br><em>Figure 10: Maggy 4.0 Voltage Regulators</em>  
</p>  

## Current Measurement

One of the new features in version 4.0 is the current measurement for each solenoid. To achieve this, 
we are using the **INA213**, a sensor specifically designed for this purpose, which allows us to obtain very 
precise current measurements. The INA213 works by measuring the voltage difference across a shunt 
resistor placed in the load circuit, which enables the calculation of the current flowing through the 
circuit. It is capable of measuring bidirectional current (both positive and negative) using a low
resistance shunt and a reference voltage. 

The reference voltage of 1.65V plays a crucial role in the operation of the INA213, as it serves as a 
reference level for its internal analog measurements. This voltage ensures that the internal analog-to
digital converter (ADC) operates optimally, thus improving the precision of measurements, even for 
very low currents. 

This new feature will provide us with real-time data on the current flowing through the solenoids. This 
will help us better understand their charging and discharging process while monitoring the card's 
power consumption and heating. 

<p align="center">  
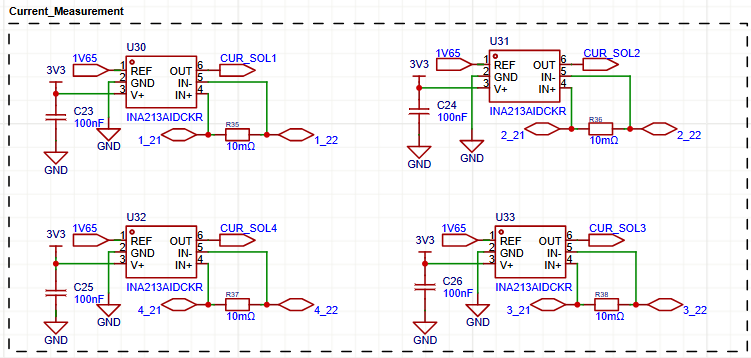
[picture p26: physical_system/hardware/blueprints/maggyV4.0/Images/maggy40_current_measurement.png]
Current Measurement Schematic
    
  <br><em>Figure 11: Maggy 4.0 Current Measurement Schematic</em>  
</p>  

The reference voltage of the INA is 1.65V, which sets the zero point for the sensor at 1.65V, allowing it 
to operate in bidirectional mode. To generate this reference voltage, we use a voltage divider from the 
3.3V supply. An operational amplifier is then used to buffer the voltage, as the voltage divider creates 
a high impedance on the VREF pin, which could affect the measurement stability.

<p align="center">  
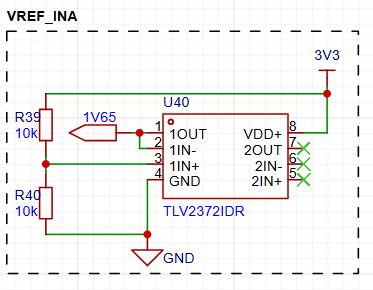
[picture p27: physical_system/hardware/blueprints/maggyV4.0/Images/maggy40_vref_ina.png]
VREF INA213 Schematic
    
  <br><em>Figure 12: VREF Circuit for INA213</em>  
</p>  

## Connectors

Maggy 4.0 introduces three new connectors:  

1. **CN1**: 8 analog inputs/outputs for signals or oscilloscope visualization.  
2. **CN2**: Connects motor driver outputs to power solenoids externally.  
3. **U6**: Enables I2C communication between the Teensy and external devices.  

| CN1 and CN2 | U6 Connector |  
|:---------------------------------------:|:---------------------------------------:|  
| _Figure 13: CN1 and CN2 Connectors_     | _Figure 14: U6 Connector_               |  

## Things to Do for Maggy 4_1 

1. **Routing Optimization** 

    Refine the routing to improve manufacturability, repairability, and overall robustness. While these adjustments are not critical to the card's functionality, they will streamline production and maintenance.
    Well-organized tracks minimize manufacturing defects and simplify repairs. Below are some recommendations to optimize the design:

    - **Package Replacement**: Use 0805 packages or larger whenever possible to facilitate troubleshooting.  
    *Explanation: Larger components are easier to handle and replace.*  

    - **Track Entry Alignment**: Ensure that tracks connect directly to the footprint from the front, not the sides.  
   *Explanation: This improves connection reliability and reduces soldering issues.*  

    - **Component Spacing and Orientation**: Leave enough space around components for soldering, even if it requires rotating them 90°.  
   *Explanation: Proper spacing supports manual work and reduces errors.*  

    - **Straight Tracks**: Remove unnecessary zigzags and aim for direct paths whenever possible.  
   *Explanation: Straight tracks are shorter and improve routing clarity.*  

    - **Track Alignment**: Keep parallel tracks grouped together to maintain alignment.  
   *Explanation: Organized routing improves reliability and reduces interference.*  

    - **Ground Plane Management**: Assign a dedicated plane to the bottom and another to the top. Avoid splitting the planes with tracks and consolidate areas with vias when necessary.  
   *Explanation: Continuous ground planes enhance electrical and thermal performance.*

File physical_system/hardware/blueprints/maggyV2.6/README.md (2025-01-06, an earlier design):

#### About the protective covers
All the components are placed slightly off-center with the outline of the PCB. The protective covers are similarly misaligned so that they align well with the PCB.

The cover with the hole is the bottom plate, with the hole giving access to the reset button on the Teensy 4.1.

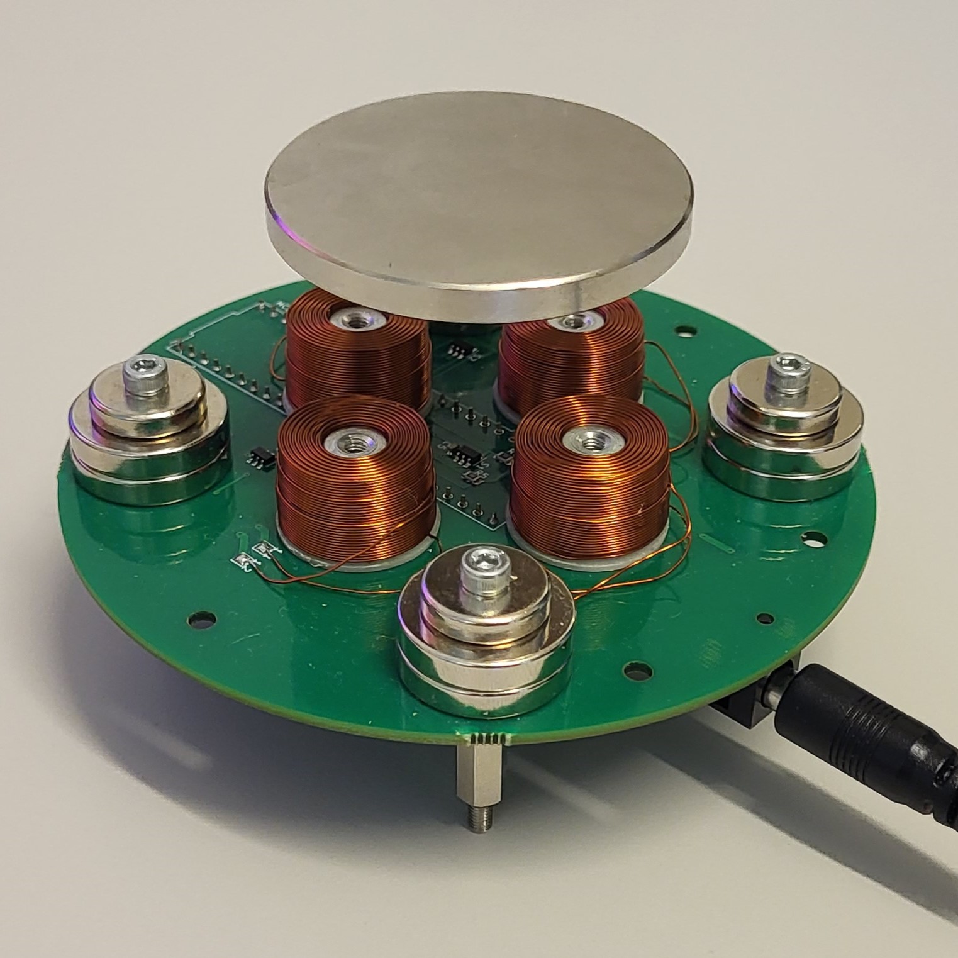
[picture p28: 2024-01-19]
media/images_and_illustrations/maggy_20_levitating.jpg

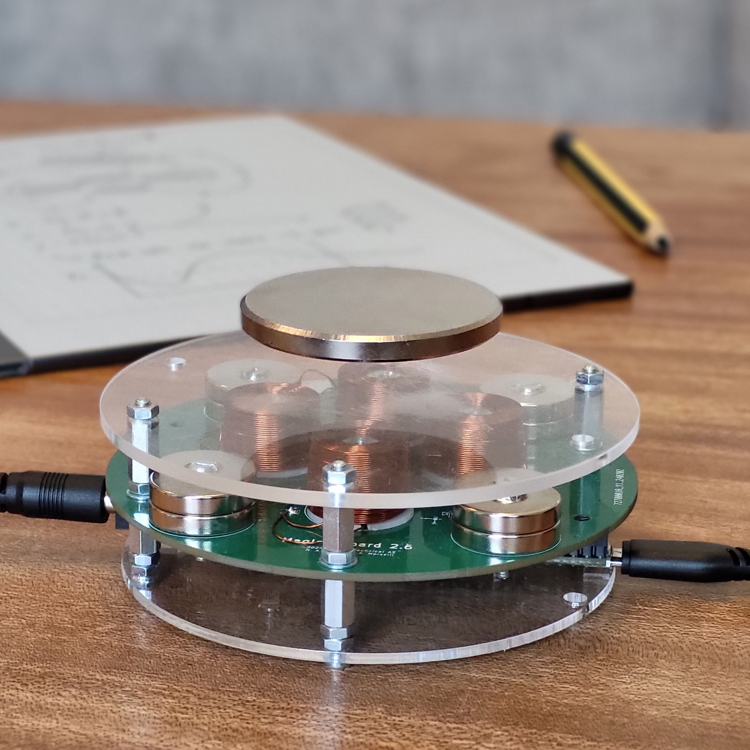
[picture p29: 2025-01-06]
media/images_and_illustrations/maggy_30_levitating.jpg

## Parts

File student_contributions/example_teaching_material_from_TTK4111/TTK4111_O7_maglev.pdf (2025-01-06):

### TTK4111 Reguleringsteknikk

Institutt for Teknisk Kybernetikk NTNU

Øving 7

Utlevert: | Mandag uke 13
Innleveringsfrist: Mandag uke 15

## Problemstilling

I forrige øving tok vi en titt pa en modell av et elektromagnetisk system illustrert i ˚
Figur 1a. I denne øvingen skal fa et gjensyn med dette systemet, men n ˚ | a skal vi ogs ˚ | a˚
anvende teorien i praksis!
Øvingen er delt i to deler: en teoretisk del og en praktisk del. Disse to skal gjennomføres separat, pa forskjellige dager. ˚
I denne øvingen skal vi anvende denne teorien i praksis, pa systemet vist i Figur ˚ | | 1b.

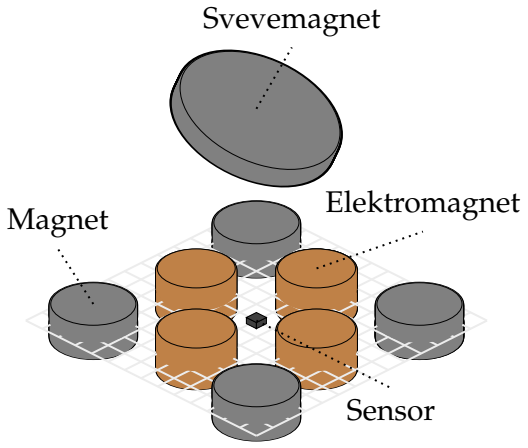
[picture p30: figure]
Elektromagnet Magnet; Svevemagnet; Sensor

(a) Illustrasjon med komponentnavn. | (b) Fysisk implementasjon (V2.6).

Fig. 1: Elektromagnetisk maglev system.

TTK4111: Øving 7 | Page 2 of 10

## 1 Del 1: Teoretisk innstilling av regulator

La oss betrakte systemet vist i Figur 1a. Dette systemet er symmetrisk langs aksene i

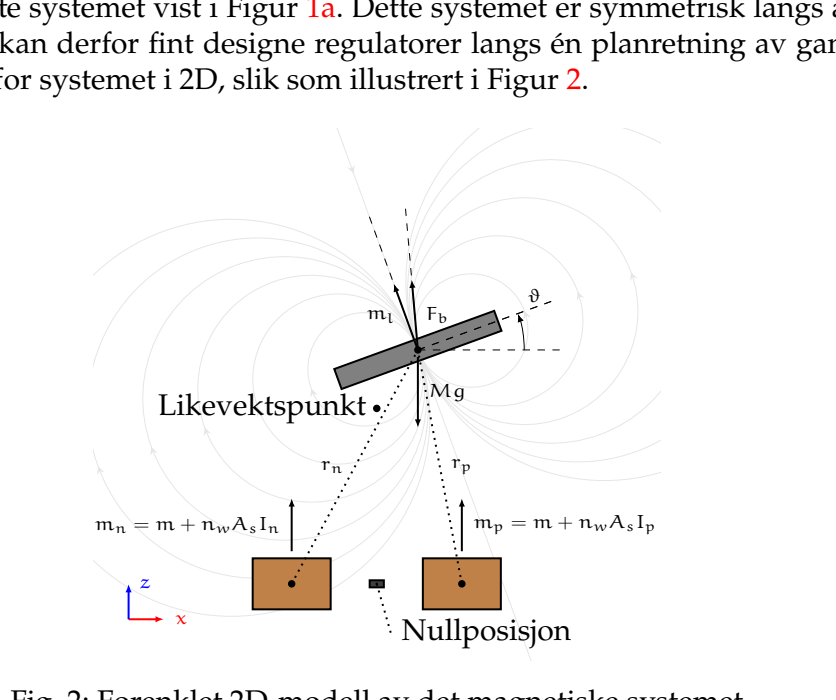
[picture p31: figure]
mn = m + nwAsIn; mp = m + nwAsIp; Nullposisjon; Likevektspunkt

planet, og vi kan derfor fint designe regulatorer langs en planretning av gangen. Vi ´ betrakter derfor systemet i 2D, slik som illustrert i Figur 2.

Fig. 2: Forenklet 2D-modell av det magnetiske systemet.

Systemet i Figur 1a bestar av en base med permanentmagneter, elektromagneter og ˚ en sensor, og en svevende magnet. Permanentmagnetene gir løftekraft, mens elektromagnetene stabiliserer systemet. Sensoren maler magnetfeltet fra den svevende mag- ˚ neten, men ogsa det som produseres av de andre magnetene og elektromagnetene. ˚ For enkelthets skyld antar vi at magnetene og elektromagnetene er punktdipoler, m.a.o.,
at størrelsen pa magnetene ikke har noe ˚ | a si, og at magnetene og elektromagnetene ˚
er magnetisk identiske, hvor strømmen i elektromagnetene kan omregnes til en ekvivalent magnetisering. Dermed kan vi gjøre enda en forenkling; vi antar at perma-
nentmagnetene og elektromagnetene kan ”plasseres” pa samme sted, slik at vi f ˚ | ar to ˚
”hybridmagneter”, som vist i Figur 2.
Med antagelsene over kan vi sette sammen en relativt kompakt modell av systemet
ved a ta utgangspunkt i det ˚ | magnetiske skalarpotensialet av magnetfeltet til hybrid-
magnetene i basen. Dette er en verdi som beskriver energien i et magnetfelt, og vi
kan bruke skalarpotensialet til den svevende magneten til a regne ut b ˚ | ade magnetisk ˚
kraft og moment. Det totale skalarpotensialet i posisjonen til den svevende magneten er gitt av

ψ = ψp + ψn =

1
4π
mp · rp
∥rp∥

3

+

mn · rn
∥rn∥

3

,

hvor p og n beskriver magnetene pa henholdsvis positiv og negativ side av nullposi- ˚ sjonen, r er avstandsvektorer fra svevemagneten til de to i basen, m er det magnetiske

TTK4111: Øving 7 | Page 3 of 10

momentet til de to hybridmagnetene, og µ0 er permeabiliteten til luft.
Fra skalarpotensialet finner vi magnetfeltet, kraften og momentet pa den svevende ˚ magneten som

B = −µ0∇ψ =⇒ Fb = −∇ (ml · B), τb = ml × B.

Kombinerer vi dette med Newtons lover og løser litt opp, far vi at bevegelsen til den ˚ svevende magneten kan beskrives av

Mx¨ = −ml

∂

2ψ
∂x∂z, | (1a)

Mz¨ = −ml

∂

2ψ
∂z²
− Mg, | (1b)

Jϑ¨ = −ml

∂ψ
∂x , | (1c)

hvor vi for enkelthets skyld har skrevet ∥ml∥ = ml.
I denne oppgaven skal vi ta utganspunkt i (1) for design av en regulator. I de utdelte kodefilene er det implementert en mer omfattende tilstandsrommodell av systemet. For testingens og sammenlignings skyld, vil vi anse den implementerte modellen som det ”ekte” systemet.
a) Det kan være lurt a ikke anvende strømmene ˚ | Ip og In direkte som padrag, men ˚
heller nettostrømmene ux og uz:

ux := Ip − In, uz := Ip + In.

Bestem Ip og In som funksjoner av ux og uz. Tegn et blokkdiagram som viser transformasjonen fra ux og uz til Ip og In.
b) Modellen i (1) er ulineær. Dersom vi lineariserer den rundt likevektspunktet vist i Figur 2 (hvor zeq er gitt, og xeq = 0, ϑeq = 0) far vi at ˚

2π
µ0mlm

Mx¨ = 3

p1

q⁹/2

x + 3

p2

q⁹/2

ϑ − 3

nwAs
m

p3

q⁷/2

ux, | (2a)

2π
µ0mlm

Mz¨ = −3

p4

q⁹/2

z − zeq
− 3

nwAs
m

p5

q⁷/2

uz, | (2b)

2π
µ0mlm

Jϑ¨ = 3

p6

q⁷/2

x −

p7

q⁷/2

ϑ + 3

nwAs
m

p8

q⁵/2

ux. | (2c)

hvor pi og q er (positive) polynomer av R og zeq. Her er m := ∥mp∥ = ∥mn∥ magnituden til det magnetiske momentet til permanentmagnetene, og As og nw tverrsnittarealet og antall viklinger i en solenoide.
Bruk den utdelte kodefilen ”numerisk linearisering.m”, og utfør en numerisk linearisering av den mer avanserte modellen, og sammenlign resultatet med (2).
Stemmer resultatet du far med ( ˚ | 2)?¹

1Merk: Likning (2) er ikke pa tilstandsromform. ˚

TTK4111: Øving 7 | Page 4 of 10
c) Sensoren maler magnetfeltet i origo i b ˚ | ade x og z retning. En lineær modell av ˚
disse malingene er gitt av ˚

yx =

3mlµ0
4πz⁴
eq

x +

mlµ0
4πz³
eq
ϑ, | (3a)

yz = −

3mlµ0
2πz⁴
eq

z +

nwAsµ0
2πz³
eq
(ux + uz). | (3b)

Bruk Matlab til a vurder observerbarheten og kontrollerbarheten til systemet. ˚ Hva skjer dersom vi ikke har tilgang til yz? Modellparametrene er oppgitt i ”numerisk linearisering.m”.
d) Anta na at det ikke er noen direkte kobling av input p ˚ | a m˚ | aling, alts ˚ | a at ˚ | D = 0 (i
en tilstandsrommodell). Med (2) og (3), vis at overføringsfunksjonene yˆx(s) = Gx(s)uˆx og yˆz(s) = Gz(s)uˆz

2 kan beskrives som³

Gx(s) = a0s

2 + a1
s

4 + b1s

2 − b2

, | Gz(s) = | a2
| s

2 + b3

,

hvor

a0 = 80, | a1 = 2.4 · 10⁵
, | a2 = 1.8,
b1 = 6.0 · 10⁵
, | b2 = 1.2 · 10⁹
, | b3 = 4.0 · 10⁹

Hva sier disse oss om stabiliteten til systemet?
e) La oss na kun betrakte systemet i x-retning. Det viser seg at en PD-regulator kan ˚
brukes til a stabilisere ˚ | Gx(s). Routh-Hurwitz kritert tilsier at følgende ma være ˚
oppfylt for at systemet skal bli stabilt

kp >

b2
a1

, kd > 0.

Finn regulatorparametre som gjør systemet praktisk stabilt.
f) Verifiser valget av regulatorparametre med Nyquist kriteriet.
g) Implementer regulatoren for det ”ekte” systemet i Simulink filen ”maglev 2d.slx”, hvor parametre og initialbetingelser er gitt. La uz = 0. Fungerer regulatoren som forventet?
h) Test regulatoren pa 3D modellen i Simulink filen ” ˚ | maglev 3d.slx”. 4

2Symbolet ”ˆ” beskriver Laplacetransformerte signaler.
3Hint: Her kan det være lurt a starte med ˚ | a bytte ut alle koeffisientene i ligning ( ˚ | 2) med positive
konstanter.
4Hint: Vi ma implementere ˚ | en regulator for hver retning i planet. ´

TTK4111: Øving 7 | | Page 5 of 10

## 2 Del 2: Eksperimentell innstilling av regulator

Systembeskrivelse

Systemet vist i Figur 1b heter Maggy V2.6, og er det samme systemet du har fatt ˚
utdelt. Maggy er 10 cm i diameter, og bestar av et kretskort med p ˚ | amonterte kompo- ˚
nenter, og en svevemagnet. Malet med Maggy er ˚ | a f ˚ a svevemagneten til ˚ | a sveve. ˚

OBS: Vær forsiktig med svevemagneten! Det er en veldig sterk magnet, men den er skjør og kan knuse. Unnga˚ a holde den i nærheten av noe magnetisk ˚ (som PC, mobil og andre magneter), og hold godt pa den i nærheten av Maggy. ˚

Sveving muliggjøres av fire par N38 neodym magneter og fire kobberspoler. Svevemagneten er en stor N38 neodym-magnet pa 5 cm i diameter, og den stabiliseres i et ˚ likevektspunkt over basen ved hjelp av tilbakekobling fra en digital Hall-effekt sensorer, synlig pa midten av brettet ˚

5
. Sensoren maler magnetfeltet i tre retninger ( ˚ | x, y, z),
med en maksimal samplingsfrekvens pa 5 kHz. ˚
Data fra sensoren mates til en Teensy 4.1 mikrokontroller. Denne drives av en ARM-
Cortex M7 mikroprosessor pa 600 MHz. Teensyen er montert p ˚ | a kretskortet sammen ˚
med andre viktige elektroniske komponenter, inkludert spenningsomformere, motordrivere og en rekke passive komponenter.
Teensy 4.1 kan programmeres direkte igjennom Arduino IDE – et programmeringsverktøy som lar oss skrive C-kode for kjøring pa mikrokontrollere. Maggy program- ˚ meres og sensordata kan leses kun med strøm fra USB kabelen pa Teensy 4.1. Maggy ˚ har derimot ogsa en dedikert strøminngang som gir strøm til elektromagnetene. ˚

5Det er to andre Hall-effekt sensorer pa Maggy, men i denne oppgaven skal vi bare bruke en av de. ˚

TTK4111: Øving 7 | | | Page 6 of 10

Utfordringer ved fysisk implementasjon

Nar vi bruker en modell for ˚ | a designe regulatorer for fysiske systemer er det mange ˚
praktiske problemer som ignoreres/utsettes til fordel for ryddigere teori. Dette er det
viktig a være klar over n ˚ | ar vi skal implementere regulatorer. De vanligste utfordrin- ˚
gene vi møter er:
- Diskretisering: I praksis males og styres alle signaler i diskret tid, da vi bruker ˚ digitale datamaskiner for regulering. Dette kan føre til en rekke utfordringer med blant annet tidsforsinkelsen, samt gjøre det vanskelig a utføre numerisk ˚ differensiering.
- Samplingsfrekvens: Høyere samplingsfrekvenser kan forbedre ytelsen, men krever mer prosesseringskraft og kan introdusere mer støy. A velge en pas- ˚ sende frekvens er en viktig avveining mellom presisjon og systemkompleksitet, da for høy frekvens kan overbelaste prosessoren, mens for lav kan føre til unøyaktigheter i responsen.
- M˚alestøy: Malingene fra sensorer vil alltid inneholde en viss grad av støy. Dette ˚
kan pavirke ytelsen p ˚ | a regulatoren, og er særlig kritisk n ˚ | ar vi er nødt til ˚ | a utføre ˚
numeriske beregninger av tidsderivat.
- Umodellert dynamikk: I den fysiske verden vil det ofte være dynamiske krefter og pavirkninger som modellen ikke har tatt høyde for, slik som friksjon, ˚
vibrasjoner, eller sma variasjoner i komponenter. Disse kan p ˚ | avirke systemets ˚
oppførsel og gjøre det vanskeligere a f ˚ a stabil kontroll basert p ˚ | a en idealisert ˚
modell.
- Transportforsinkelse: I mange systemer er det en forsinkelse mellom maling, ˚ prosessering, og handling, som ikke alltid er modellert (lav samplingsfrekvens er et opphav til dette). Slike forsinkelser kan føre til ustabilitet og ma taes høyde ˚ for i regulatordesign, spesielt for systemer hvor det oppstar raske endringer. ˚
- Begrensninger i aktuatorer: I praksis har aktuatorer, som motorer og elektromagneter, fysiske begrensninger pa kraft, hastighet, og respons. Disse begrens- ˚ ningene kan føre til metningseffekter der systemet ikke kan reagere sa raskt eller ˚ sterkt som ønsket, noe som kan føre til ustabilitet eller redusert kontrollpresisjon.
- Sensoroppløsning og kalibrering: Sensorer har begrenset oppløsning og ma˚
ofte kalibreres nøyaktig for a sikre riktige m ˚ | alinger. Lav oppløsning eller d ˚ | arlig ˚
kalibrering kan føre til unøyaktige malinger, som kan p ˚ | avirke regulatorens ytel- ˚
se og systemets stabilitet.
Samtlige av de ovennevnte utfordringene finnes ogsa i Maggy, og det kan være nyttig ˚
a tenke over hvordan disse p ˚ | avirker regulatortuningsprosessen. Noen av disse vil vi ˚
ogsa ta direkte h ˚ | and om senere i øvingen. ˚

TTK4111: Øving 7 | | Page 7 of 10

Oppgave 1: System & oppsett
Arduino er et kjent verktøy for enkel C-kode programmering og kompilering til mikro-
kontrollere. I denne oppgaven skal vi sette opp Arduino for a kunne kjøre v ˚ | | ar egen ˚
kode pa Maggy. ˚
a) Installer siste versjon av Arduino IDE. (https://www.arduino.cc/en/software)
b) Nar du starter Arduino IDE vil du se en tom Arduino sketch. G ˚ | a til ”File ˚ | >> Pre-
ferences” (WINDOWS) eller ”ARDUINO IDE >> Settings” (MAC), og lokaliser ”Additional boards manager URLs”-feltet pa bunnen av vinduet, slik som vist ˚ i Figur 3. Kopier følgende lenke inn i feltet:
| https://www.pjrc.com/teensy/package teensy index.json (https://www.pjrc.com/teensy/package_teensy_index.json)
Bruk komma for separasjon dersom det allerede star noe skrevet i feltet. ˚

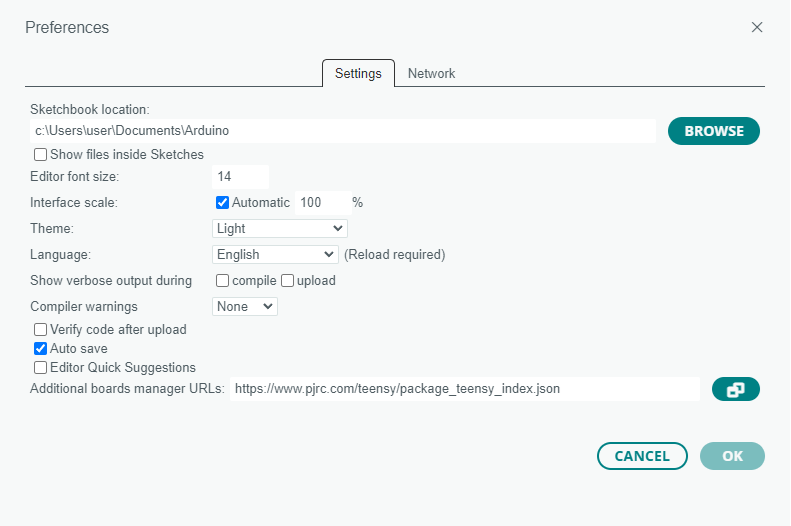
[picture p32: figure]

Fig. 3: Arduino IDE preferanser.

TTK4111: Øving 7 | | Page 8 of 10
c) Trykk pa ”boards manager” i verktøylinjen til venstre p ˚ | a forsiden p ˚ | a Arduino ˚
IDE. Søk ”Teensy” og installer Teensy pakken av Paul Stoffregen, slik som vist i Figur 4.
d) Trykk pa ”library manager” p ˚ | a verktøylinjen til venstre og søk ”TLE493D” i søkefeltet ˚
og installer pakken fra ”Infineon Technologies”, som vist i Figur 5.

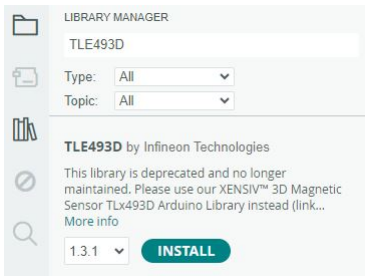
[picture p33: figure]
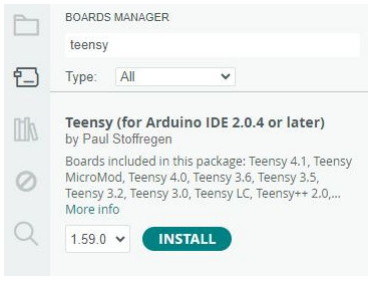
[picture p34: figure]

Fig. 4: Arduino IDE boards manager. | Fig. 5: Arduino IDE library manager

OBS: Før du setter strøm pa Maggy, fjern den store diskmagneten fra systemet. ˚ Skriptene vi skal kjøre senere vil kjøre rutiner for fjerning av bias i malingene, ˚ og vi ønsker ikke a fjerne effekten av svevemagneten. ˚

e) Koble Maggy og Teensy til PCen med en micro-USB kabel.⁶ Sjekk at du er i stand
til a laste opp en blank sketch ved ˚ | a velge COM-porten til Teensy 4.1 fra ”Se- ˚
lect board” drop-down menyen pa toppen av vinduet. Trykk ”Upload” for ˚ | a˚
kompilere og laste sketchen til Teensy 4.1. Du vil se mye rød tekst i konsollvinduet under kompilering og opplasting, men det skal ha gatt fint dersom de siste ˚ tekstlinjene er slik som vist i Figur 6.

Fig. 6: Melding i Arduino IDE kommandovindu ved vellykket kompilering.

6Dersom Teensyen ikke blir gjenkjent av PC-en, koble til ekstern strøm til Maggy ved a plugge inn ˚ strømkabelen pa motsatt side av USB-porten. ˚

TTK4111: Øving 7 | | Page 9 of 10

Oppgave 2: Systemtesting & Kalibrering
Før vi lager en regulator burde vi teste at systemet fungerer som forventet. Vi ønsker
ogsa˚ a kalibrere sensoren ved ˚ | a fjerne uønskede effekter fra m ˚ | alingene. Siden ingen ˚
systemer er helt like, kan asymmetrier og andre forstyrrelser skape utfordringer ved regulering.
a) Kompiler og last opp skriptet ”sensortest.ino” til Maggy.
b) Trykk pa ”serial plotter” i høyre hjørne. Du skal n ˚ | a se et plot med m ˚ | aledata som ˚
sendes fra magnetsensoren i Maggy. Bx, By og Bz er hhv. magnetfeltet malt i ˚ | x,
y og z retning. Hvordan ser malesignalene ut? Flytt litt rundt p ˚ | a Maggy. Endrer ˚
signalene seg?
c) Hold svevemagneten i nærheten av Maggy for a se hvordan den p ˚ | avirker signale- ˚
ne. Hvordan endrer signalene seg nar du flytter p ˚ | a svevemagneten? ˚
OBS: Elektromagnetene blir varme om de star p ˚ | a for lenge. Trekk ut ˚
strømkabelen nar Maggy ikke er i bruk, for ˚ | a unng ˚ | a at elektromagnetene blir ˚
overopphetet.
d) Last opp skriptet ”elektromagnettest.ino” til Maggy. Seriel plotteren vil na vise ˚ kontrollsignal til elektromagnetene, samt sensormalingene fra tidligere. Hvor- ˚ dan endrer sensormalingene seg med endring i strøm i elektromagnetene? Pass ˚
pa at strømkabelen er koblet i slik at elektromagnetene f ˚ | | ar strøm. ˚
De foregaende oppgavene viser hvordan sensorene plukker opp m ˚ | | alinger fra perma- ˚
nentmagnetene, elektromagnetene og svevemagneten. Vi ønsker kun a m˚ | ale magnet- ˚
feltet til svevemagneten. Vi kan heldigvis kvitte oss med mesteparten av effektene fra
de andre komponentene ved a m˚ ale hva de er n ˚ | ar svevemagneten ikke er til stede, og ˚
deretter kompensere for disse i koden.
e) Last opp sketchen ”beregning direkte foroverkobling.ino”. Denne filen beregner
verdier for hvordan malingene blir p ˚ | avirket av elektromagnetene. La skriptet ˚
kjøre uten svevemagneten i nærheten og les av verdiene for kompensasjon for de ulike elektromagnetene fra ”serial monitor”.
f) Legg disse verdiene inn i toppen av ”elektromagnettest.ino” og velg ”remove mean
= True” og ”remove direct feedthrough = True”. Kompiler pa nytt. Har vi klart ˚ | a˚
kvitte oss med effekten av permanentmagneten og elektromagnetene i malingene? ˚
Test om malingene endrer seg n ˚ | ar du beveger svevemagneten rundt Maggy. ˚

TTK4111: Øving 7 | | Page 10 of 10

Oppgave 3: Eksperimentell innstilling av regulator
Ta utgangspunkt i den utleverte filen ”PD control.ino”.⁷ Filen inneholder riktig oppsett av Teensy, samt filter for fjerning av støy og andre forstyrrelser, og en halvferdig PD-regulator. I denne oppgaven skal du justere kp og kd i filen slik at magneten til slutt svever.
Det er verdt a merke seg at verdiene for ˚ | kp og kd for Maggy har en annen skalering
enn i simulering – da inngangssignalene ikke er strøm, og utgangssignalene er oppgitt i mT og ikke T –, men at forholdet mellom de to kontrollparametrene burde være noenlunde likt. Som en pekepinn burde verdiene være omtrent

kp ∈ [100, 600],
kd ∈ [0, 2].
a) Apne ”PD ˚ | regulator.ino” og sett kalibreringsverdiene slik som i forrige oppgave.
b) Juster verdiene for kp og kd for a oppn ˚ | a stabil sveving. Start med sm ˚ | a verdier ˚
og øk gradvis. Du skal kunne føle at svevemagneten vil naturlig legge seg i en ”grop” over midten av Maggy nar regulatoren er tunet. ˚

7Denne filen inneholder en terskel som gjør at det ikke gar strøm i elektromagnetene med mindre ˚ svevemagneten er nærme nok. Du vil kunne se dette som et ”hopp”i dataen og merke at det rykker litt i magneten.

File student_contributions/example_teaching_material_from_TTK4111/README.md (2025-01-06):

# What is this?
This is an assigment that was given for Maggy V2.6 to a class of about 100 students in the course TTK4111 at NTNU in the fall of 2024. The assigment contains one "experimental" and one "simulation based" assigment, ment to give physical understanding and insight into the system. The assigment is written in Norwegian.

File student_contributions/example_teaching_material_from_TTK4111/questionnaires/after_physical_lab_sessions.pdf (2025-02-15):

## Fysisk - Spm etter samling 1 for A, Spm etter samling 2 for B

Informasjon til deltakere

Du inviteres til å delta i en undersøkelse om persipert læringsutbytte og mestringsforventning i forbindelse med TTK4111 og fremtidige karrieremuligheter. Studien gjennomføres av NTNU og har som mål å få en bedre forståelse av hvordan labøvingene fungerer for studentene i emnet.

Viktig informasjon om undersøkelsen:

Spørsmålene vil dekke områder som labøvinger, forventninger til faget og forventninger til karriere. Undersøkelsen tar ca. 8-10 minutter å gjennomføre. Deltakelse er helt frivillig, og du kan når som helst trekke deg fra undersøkelsen uten å oppgi en grunn og uten negative konsekvenser. Data som samles inn vil brukes til å analysere studentenes opplevelse av labøvinger og tilknyttede læringsutbytter. Personopplysninger vil bli brukt for å koble informasjon sammen, og vi vil sørge for at disse opplysningene behandles med høy grad av konfidensialitet. Personopplysninger vil bli lagret i opptil to uker etter siste innhenting før de slettes.

Kontaktinformasjon

Dersom du har spørsmål om undersøkelsen eller ønsker mer informasjon, kan du kontakte prosjektledere:
Morten Dinhoff Pedersen: morten.d.pedersen@ntnu.no
Hans Alvar Engmark: hans.a.engmark@ntnu.no
Damiano Varagnolo: damiano.varagnolo@ntnu.no Lasse Mostad: lasse.mostad@ntnu.no

Jeg vil delta i denne studien.
Ja
Nei
Brukernavn
Vennligst skriv inn de 4 siste tallene i ditt telefonnummer. Jeg identifiserer meg som
Kvinne
Mann
Annet
Nå som du har gjennomført den fysiske samlingen...
Ferdighetsutvikling
På en skala fra 1-7.
Etter å ha jobbet med å implementere en kontroller på et fysisk system, hvor sikker er du på å kunne implementere og feilsøke innebygde kontrollsystemer?
Ekstremt sikker

Svært sikker
Litt sikker
Verken sikker eller usikker Litt usikker
Svært usikker
Ekstremt usikker
Sikkerhet
Hvor sannsynlig er det at du vil starte et komplekst kontrollprosjekt på egenhånd etter denne lab-opplevelsen?
Ekstremt sannsynlig
Svært sannsynlig
Litt sannsynlig
Verken sannsynlig eller usannsynlig Litt usannsynlig
Svært usannsynlig
Ekstremt usannsynlig
Påvirket denne lab-opplevelsen din interesse og trygghet til å utforske mer avanserte temaer innen elektronikk og innebygde systemer?
Velg på en skala fra 0-5
Er dette din andre samling?
Du vil bli sendt til et tileggskjema
Ja
Nei

Generert: 2025-02-15 10:47:46.

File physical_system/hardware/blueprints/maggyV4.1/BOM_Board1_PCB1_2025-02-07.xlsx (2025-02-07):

No. | Quantity | Comment | Designator | Footprint | Value | Manufacturer Part | Manufacturer | Supplier Part | Supplier
1 | 4 | 10uF | C1,C2,C3,C4 | C0805 | 10uF
2 | 17 | 100nF | C5,C7,C8,C9,C10,C11,C12,C13,C14,C15,C17,C19,C21,C23,C24,C25,C26 | C0603 | 100nF
3 | 2 | 1uF | C6,C27 | C0805 | 1uF
4 | 4 | 100uF | C16,C18,C20,C22 | CAP-SMD_BD6.3-L6.6-W6.6-LS7.2-FD | 100uF | RST100UF35V009 | KNSCHA(科尼盛) | C4747966 | LCSC
5 | 1 | 430451000 | CN1 | CONN-TH_43045-1000 |  | 430451000 | MOLEX | C122421 | LCSC
6 | 1 | 0430450800 | CN2 | CONN-TH_0430450800 |  | 0430450800 | MOLEX | C122422 | LCSC
7 | 4 | XL-1608SYGC-06 | LED1,LED2,LED3,LED4 | LED0603-RD_GREEN |  | XL-1608SYGC-06 | XINGLIGHT(成兴光) | C965805 | LCSC
8 | 21 | 1k2 | R1,R2,R6,R7,R8,R9,R10,R11,R12,R13,R14,R15,R16,R17,R18,R19,R20,R21,R32,R33,R34 | R0805 | 1k2
9 | 2 | 56 | R3,R28 | R0603 | 56
10 | 1 | 120 | R4 | R0603 | 120
11 | 1 | 200 | R5 | R0603 | 200
12 | 4 | 0.3 | R22,R23,R24,R25 | R1206 | 0.3
13 | 1 | 24k | R26 | R0805 | 24k
14 | 1 | 1k | R27 | R0805 | 1k
15 | 3 | 10k | R29,R39,R40 | R0805 | 10k
16 | 4 | 15mΩ | R35,R36,R37,R38 | R1206 | 15mΩ | 1206W3F100MT5E | UNI-ROYAL(厚声) |  | LCSC
17 | 1 | LM1117S-5.0 | U1 | SOT-223-3_L6.5-W3.4-P2.30-LS7.0-BR |  | LM1117S-5.0 | HTC | C126028 | LCSC
18 | 1 | LM1117S-3.3 | U2 | SOT-223-3_L6.5-W3.4-P2.30-LS7.0-BR |  | LM1117S-3.3 | HTC | C126027 | LCSC
19 | 1 | CH224K | U3 | ESSOP-10_L4.9-W3.9-P1.0-LS6.0-TL-EP |  | CH224K | WCH(南京沁恒) | C970725 | LCSC
20 | 2 | X6511FV-24-C85D32 | U4,U5 | HDR-TH_24P-P2.54-V-F |  | X6511FV-24-C85D32 | XKB Connectivity(中国星坤) | C2883741 | LCSC
21 | 1 | XH-4AW米色 | U6 | CONN-TH_XH2.54-4AW |  | XH-4AW米色 | BOOMELE(博穆精密) | C146115 | LCSC
22 | 1 | TCA9548APWR | U7 | TSSOP-24_L7.8-W4.4-P0.65-LS6.4-BL |  | TCA9548APWR | TI(德州仪器) | C130026 | LCSC
23 | 8 | TLV493DA1B6HTSA2 | U10,U11,U12,U13,U14,U15,U16,U17 | SOP-6_L3.0-W1.5-P0.95-LS2.5-BR |  | TLV493DA1B6HTSA2 | Infineon(英飞凌) | C126688 | LCSC
24 | 4 | A4950ELJTR-T | U20,U21,U22,U23 | SOIC-8_L4.9-W3.9-P1.27-LS6.0-BL-EP |  | A4950ELJTR-T | ALLEGRO(美国埃戈罗) | C82404 | LCSC
25 | 1 | BZT52C6V2 | U27 | SOD-123_L2.7-W1.6-LS3.7-RD |  | BZT52C6V2 | CJ(江苏长电/长晶) | C2910064 | LCSC
26 | 4 | INA214AIDCKR | U30,U31,U32,U33 | SC-70-6_L2.2-W1.3-P0.65-LS2.2-BR |  | INA214AIDCKR | TI(德州仪器) | C105240 | LCSC
27 | 1 | TLV2372IDR | U40 | SOIC-8_L4.9-W3.9-P1.27-LS6.0-BL |  | TLV2372IDR | TI(德州仪器) | C27204 | LCSC
28 | 4 | XY308-2.54-2P | U50,U51,U52,U53 | CONN-TH_XY308-2.54-2P |  | XY308-2.54-2P | XINLAIYA(新莱亚) | C557685 | LCSC
29 | 1 | TYPE-C-31-M-12 | USBC1 | USB-C_SMD-TYPE-C-31-M-12 |  | TYPE-C-31-M-12 | 韩国韩荣 | C165948 | LCSC

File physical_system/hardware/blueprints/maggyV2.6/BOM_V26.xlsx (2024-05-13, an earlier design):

Type | Link | Part ID | Stock | Needed | Unit price | Total price
Barrel jack connector | https://www.digikey.no/no/products/detail/cui-devices/PJ-036AH-SMT-TR/1530971 | PJ-036AH-SMT-TR | 42522 | 1 | 13.01kr | 13.01kr
Anti static pad | https://www.digikey.no/no/products/detail/sparkfun-electronics/TOL-14672/8702492?productid=8702492&gad_source=1 | TOL-14672 | 649 | 0 | 119.00 kr | 0.00kr
Anti static bag | https://www.digikey.no/no/products/detail/scs/30068/3430458 | 30068 | 184246 | 0 | 2.86 kr | 0.00kr
Power supply | https://www.digikey.no/en/products/detail/xp-power/VEL36US120-EU-JA/6220847 | VEL36US120-EU-JA | 63 | 1 | 189.00 kr | 189.00kr
Teensy 4.1 | https://www.digikey.no/no/products/detail/sparkfun-electronics/DEV-16996/13158152 | DEV-16996 | 1478 | 1 | 396.00 kr | 396.00kr
Hall-effect sensor A0 | https://no.mouser.com/ProductDetail/Infineon-Technologies/TLE493DW2B6A0HTSA1?qs=qpJ%252B%252B%252Bdg6p1ZWZo3xqeg4Q%3D%3D | TLE493DW2B6A0HTSA1 | 4993 | 1 | 19.64kr | 19.64kr
Hall-effect sensor A1 | https://no.mouser.com/ProductDetail/Infineon-Technologies/TLE493DW2B6A1HTSA1?qs=qpJ%252B%252B%252Bdg6p2GsXYBHjVLRg%3D%3D | TLE493DW2B6A1HTSA1 | 910 | 1 | 19.64kr | 19.64kr
Hall-effect sensor A2 | https://no.mouser.com/ProductDetail/Infineon-Technologies/TLE493DW2B6A2HTSA1?qs=qpJ%252B%252B%252Bdg6p3sDlfUVyprJw%3D%3D&gad_source=1 | TLE493DW2B6A2HTSA1 | 1318 | 1 | 21.83kr | 21.83kr
Female header 24P | https://no.mouser.com/ProductDetail/Samtec/SSM-124-L-SV?qs=rU5fayqh%252BE0vrs1Fgp%252Btrw%3D%3D | SSM-124-L-SV | 140 | 2 | 40.19kr | 80.38kr
Solenoids | https://www.aliexpress.com/item/4000076659177.html?curPageLogUid=W7mtjk8XbjMA&utparam-url=scene%3Asearch%7Cquery_from%3A | N/A | N/A | 4 | 14.00kr | 56.00kr
Big magnet | https://supermagneter.no/diskmagnet-50x5mm-id752 | N/A | N/A | 1 | 299.00kr | 299.00kr
Small magnet | https://supermagneter.no/magnet-med-monteringshull-20x4mm-id794 | N/A | N/A | 12 | 49.00kr | 588.00kr
SUM |  |  |  |  |  | 1682.50kr

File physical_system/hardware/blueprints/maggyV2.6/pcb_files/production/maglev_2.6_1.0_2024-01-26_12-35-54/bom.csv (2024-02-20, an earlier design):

Designator | Footprint | Quantity | Value | LCSC Part #
C1, C2, C3, C4 | 0805 | 4 | 10uF
C10, C12, C14, C8 | CP_Elec_6.3x7.7 | 4 | 100uF
C11, C13, C15, C5, C6, C7, C9 | 0603 | 7 | 100nF
J1 | BarrelJack_CUI_PJ-036AH-SMT_Horizontal | 1 | PJ-036AH-SMT-TR
J2, J3 | PinSocket_1x24_P2.54mm_Vertical_SMD_Pin1Left | 2 | SSM-124-L-SV
M1, M2, M3, M4 | SOIC-8-1EP_3.9x4.9mm_P1.27mm_EP2.41x3.3mm | 4 | A4950E
R1, R2, R3, R4 | 1206 | 4 | 0.45
R5, R6 | 0805 | 2 | 1K2
S1 | SOT-23-6 | 1 | TLE493DW1B6A0
S2 | SOT-23-6 | 1 | TLE493DW1B6A1
S3 | SOT-23-6 | 1 | TLE493DW1B6A2
U1 | SOT-223-3_TabPin2 | 1 | LM1117S-3.3
U2 | SOT-223-3_TabPin2 | 1 | LM1117S-5.0

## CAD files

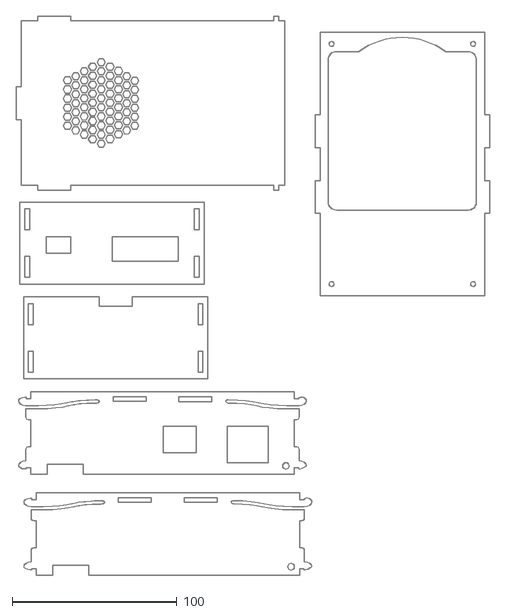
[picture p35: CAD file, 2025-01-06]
physical_system/hardware/blueprints/maggyV4.1/Enclosure/V6_Enclosure_V40.dxf
287.5 x 339.7

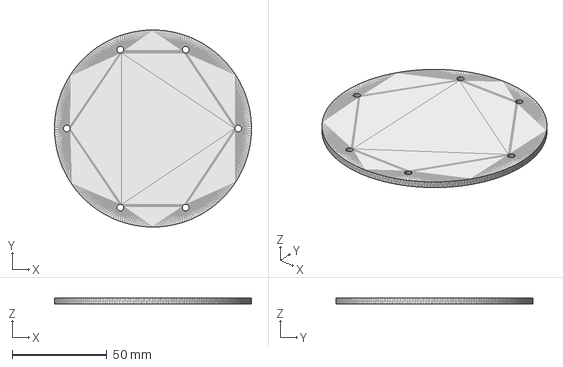
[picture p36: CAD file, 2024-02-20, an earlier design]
physical_system/hardware/blueprints/maggyV2.6/protective_cover_cad.step
104.0 x 104.0 x 3.00 mm

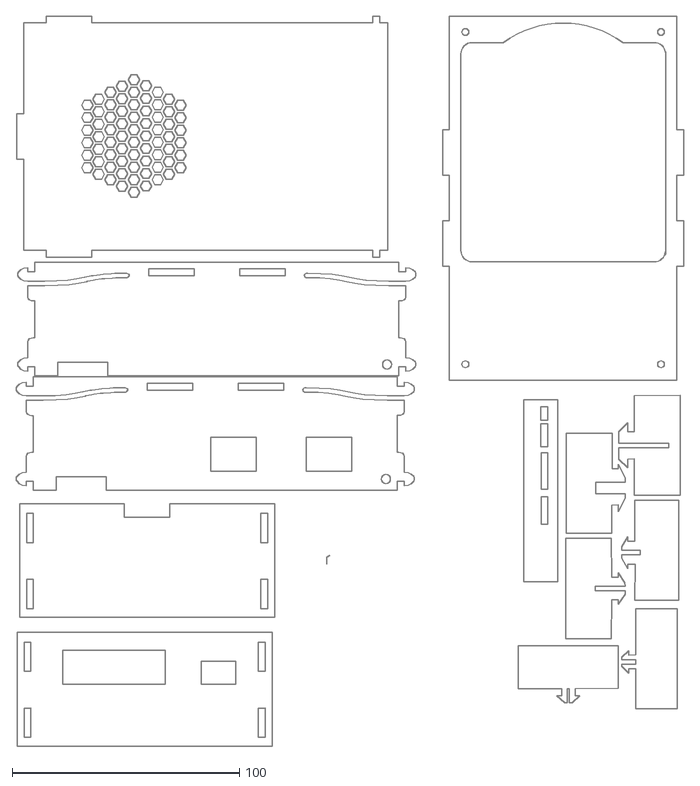
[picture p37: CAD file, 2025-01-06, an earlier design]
physical_system/hardware/blueprints/maggyV4.1/Enclosure/old/V3_Enclosure_V40.dxf
293.4 x 320.9

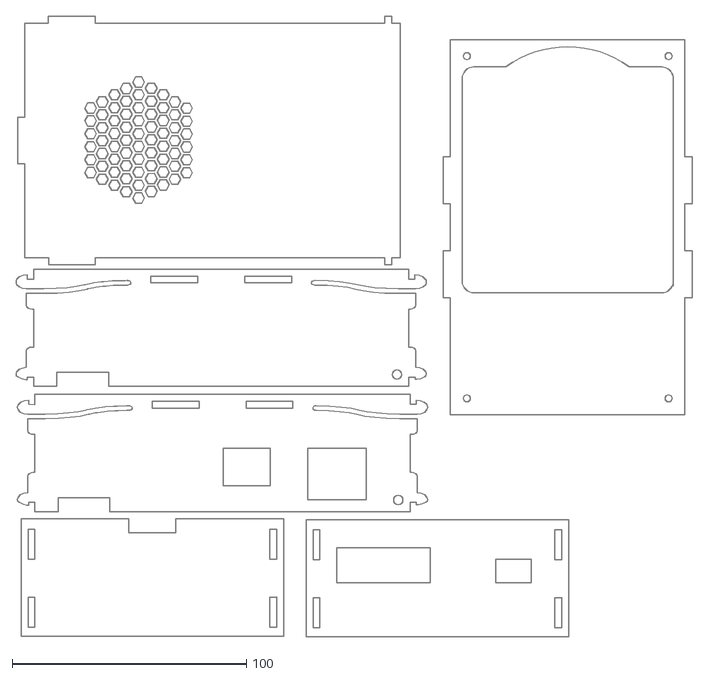
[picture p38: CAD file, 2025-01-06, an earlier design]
physical_system/hardware/blueprints/maggyV4.1/Enclosure/old/V5_Enclosure_V40.dxf
288.3 x 264.6

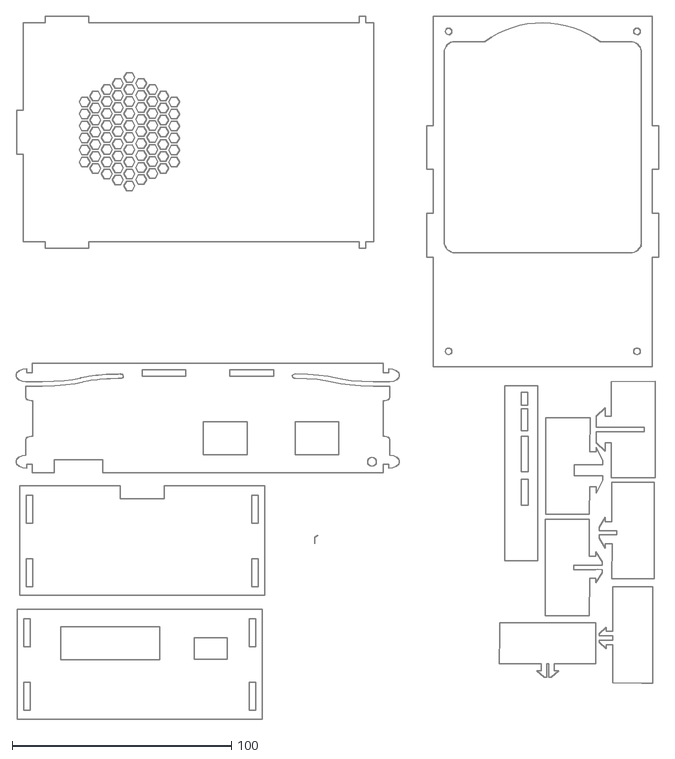
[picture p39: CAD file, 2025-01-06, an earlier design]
physical_system/hardware/blueprints/maggyV4.1/Enclosure/old/V4_Enclosure_V40.dxf
293.4 x 320.9

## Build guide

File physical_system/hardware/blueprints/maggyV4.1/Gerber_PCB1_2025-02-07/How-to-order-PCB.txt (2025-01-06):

How to Order PCB

Please refer to:
https://prodocs.easyeda.com/en/pcb/order-order-pcb/index.html

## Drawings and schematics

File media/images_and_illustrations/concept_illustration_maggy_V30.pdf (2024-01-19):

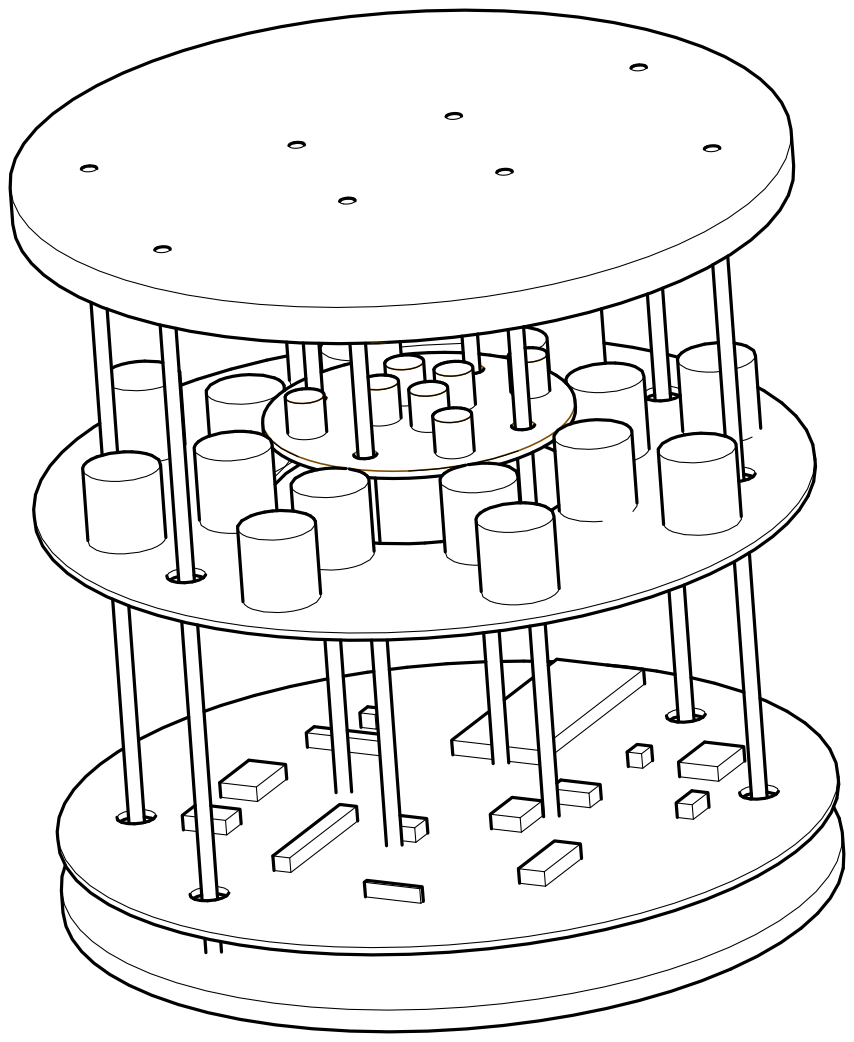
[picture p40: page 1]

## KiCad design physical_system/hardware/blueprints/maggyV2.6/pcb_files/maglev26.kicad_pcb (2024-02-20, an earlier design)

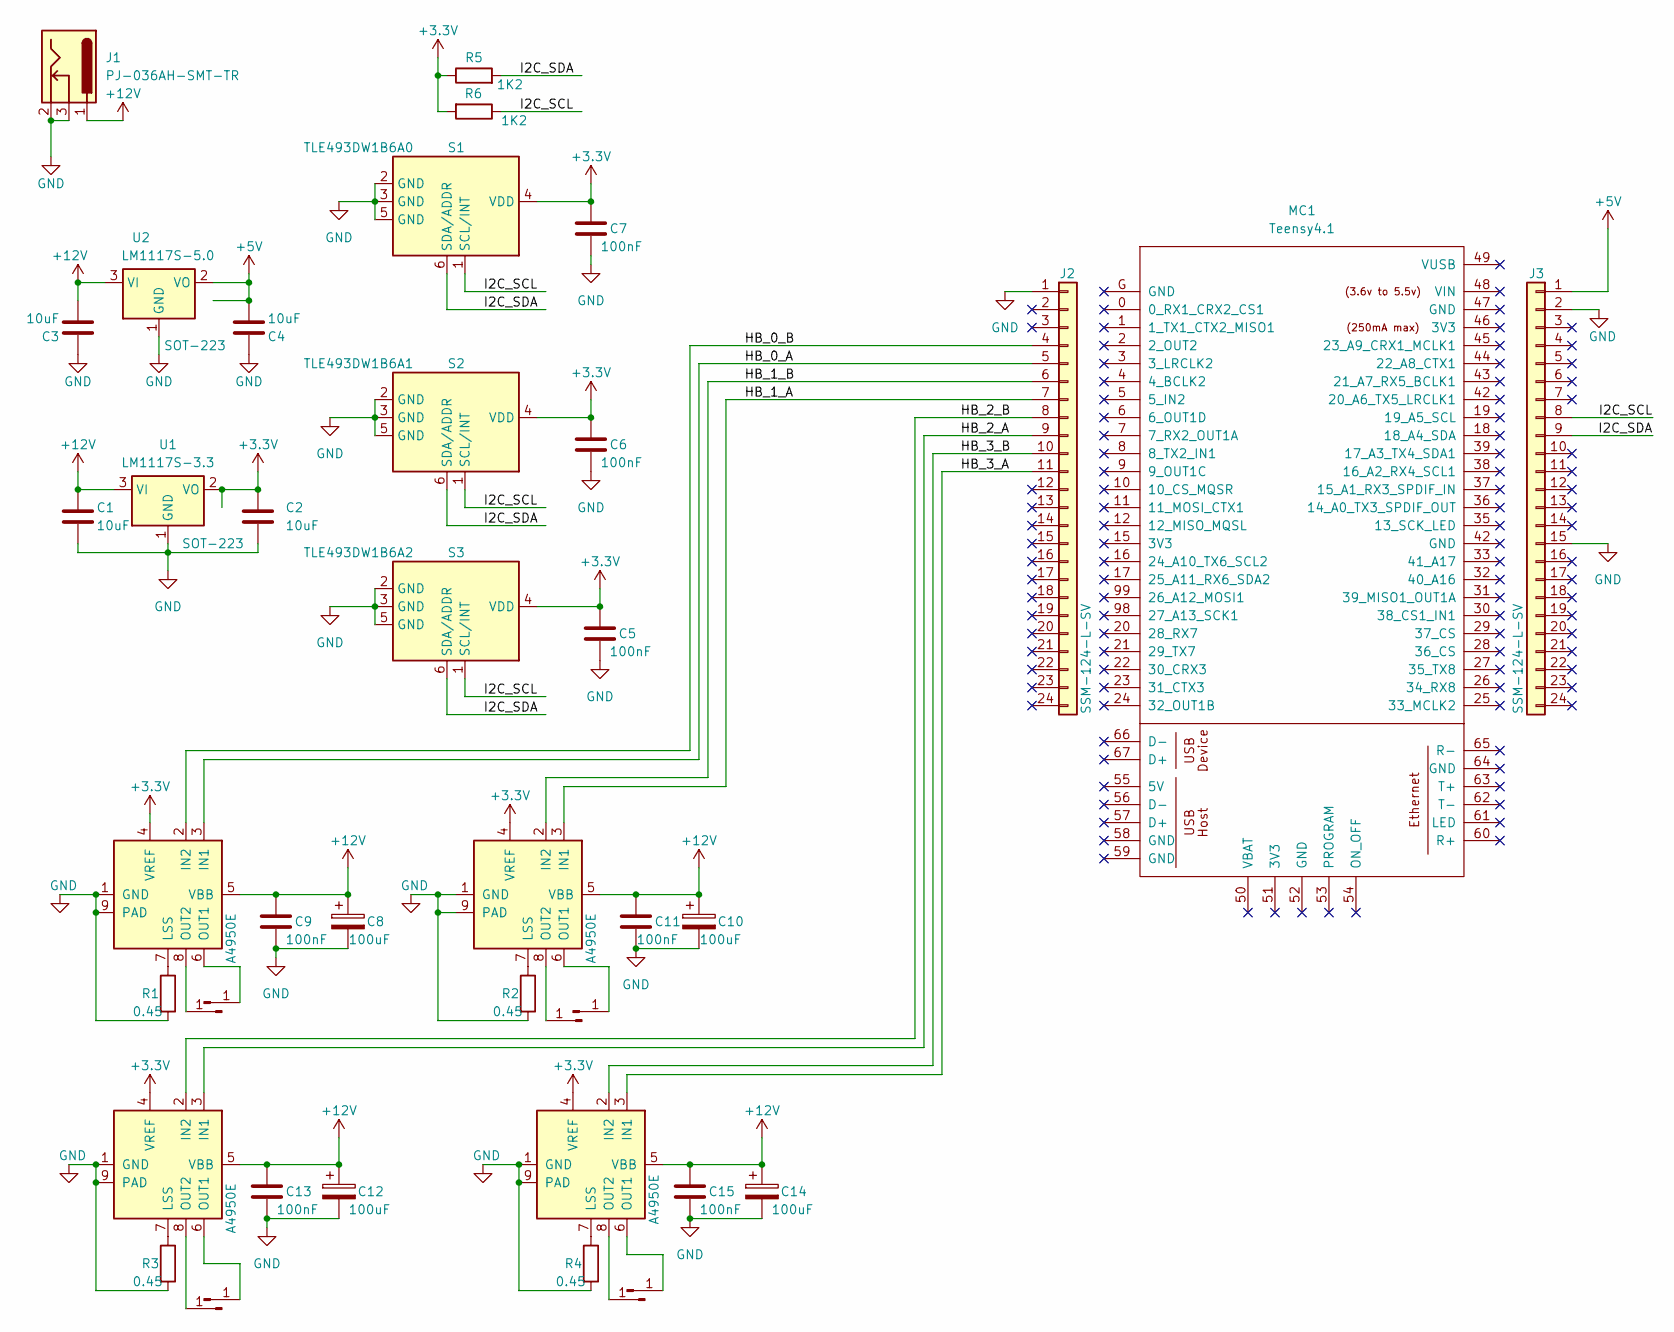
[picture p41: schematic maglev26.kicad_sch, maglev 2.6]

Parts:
1_1, 1_2, 2_1, 2_2, 3_1, 3_2, 4_1, 4_2: solenoid; TestPoint_Pad_1.5x1.5mm
C1, C2, C3, C4: 10uF; C_0805_2012Metric
C5, C6, C7, C9, C11, C13, C15: 100nF; C_0603_1608Metric
C8, C10, C12, C14: 100uF; CP_Elec_6.3x7.7
J1: PJ-036AH-SMT-TR; BarrelJack_CUI_PJ-036AH-SMT_Horizontal
J2, J3: SSM-124-L-SV; PinSocket_1x24_P2.54mm_Vertical_SMD_Pin1Left
M1, M2, M3, M4: A4950E; SOIC-8-1EP_3.9x4.9mm_P1.27mm_EP2.41x3.3mm
MC1: Teensy4.1; teensy 4.1
R1, R2, R3, R4: 0.45; R_1206_3216Metric_Pad1.30x1.75mm_HandSolder
R5, R6: 1K2; R_0805_2012Metric
S1: TLE493DW1B6A0; SOT-23-6
S2: TLE493DW1B6A1; SOT-23-6
S3: TLE493DW1B6A2; SOT-23-6
U1: LM1117S-3.3; SOT-223-3_TabPin2
U2: LM1117S-5.0; SOT-223-3_TabPin2

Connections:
+3.3V: C2.1, C5.2, C6.2, C7.2, M1.4 (VREF), M2.4 (VREF), M3.4 (VREF), M4.4 (VREF), R5.1, R6.2, S1.4 (VDD), S2.4 (VDD), S3.4 (VDD), U1.2 (VO); also elsewhere on the board
+5V: C4.2, J3.1, U2.2 (VO); also elsewhere on the board
+12V: C1.1, C3.2, C8.1, C9.1, C10.1, C11.1, C12.1, C13.1, C14.1, C15.1, J1.1, M1.5 (VBB), M2.5 (VBB), M3.5 (VBB), M4.5 (VBB), U1.3 (VI), U2.3 (VI); also elsewhere on the board
/HB_0_A: J2.5, M1.3 (IN1)
/HB_0_B: J2.4, M1.2 (IN2)
/HB_1_A: J2.7, M2.3 (IN1)
/HB_1_B: J2.6, M2.2 (IN2)
/HB_2_A: J2.9, M3.3 (IN1)
/HB_2_B: J2.8, M3.2 (IN2)
/HB_3_A: J2.11, M4.3 (IN1)
/HB_3_B: J2.10, M4.2 (IN2)
/I2C_SCL: J3.8, R6.1, S1.1 (SCL/INT), S2.1 (SCL/INT), S3.1 (SCL/INT)
/I2C_SDA: J3.9, R5.2, S1.6 (SDA/ADDR), S2.6 (SDA/ADDR), S3.6 (SDA/ADDR)
GND: C1.2, C2.2, C3.1, C4.1, C5.1, C6.1, C7.1, C8.2, C9.2, C10.2, C11.2, C12.2, C13.2, C14.2, C15.2, J1.2, J1.3, J2.1, J3.2, J3.15, M1.1 (GND), M1.9 (PAD), M2.1 (GND), M2.9 (PAD), M3.1 (GND), M3.9 (PAD), M4.1 (GND), M4.9 (PAD), R1.2, R2.2, R3.2, R4.2, S1.2 (GND), S1.3 (GND), S1.5 (GND), S2.2 (GND), S2.3 (GND), S2.5 (GND), S3.2 (GND), S3.3 (GND), S3.5 (GND), U1.1 (GND), U2.1 (GND); also elsewhere on the board
unnamed: 1_1.1, M1.6 (OUT1)
unnamed: 1_2.1, M1.8 (OUT2)
unnamed: 2_1.1, M2.6 (OUT1)
unnamed: 2_2.1, M2.8 (OUT2)
unnamed: 3_1.1, M3.6 (OUT1)
unnamed: 3_2.1, M3.8 (OUT2)
unnamed: 4_1.1, M4.6 (OUT1)
unnamed: 4_2.1, M4.8 (OUT2)
unnamed: M1.7 (LSS), R1.1
unnamed: M2.7 (LSS), R2.1
unnamed: M3.7 (LSS), R3.1
unnamed: M4.7 (LSS), R4.1

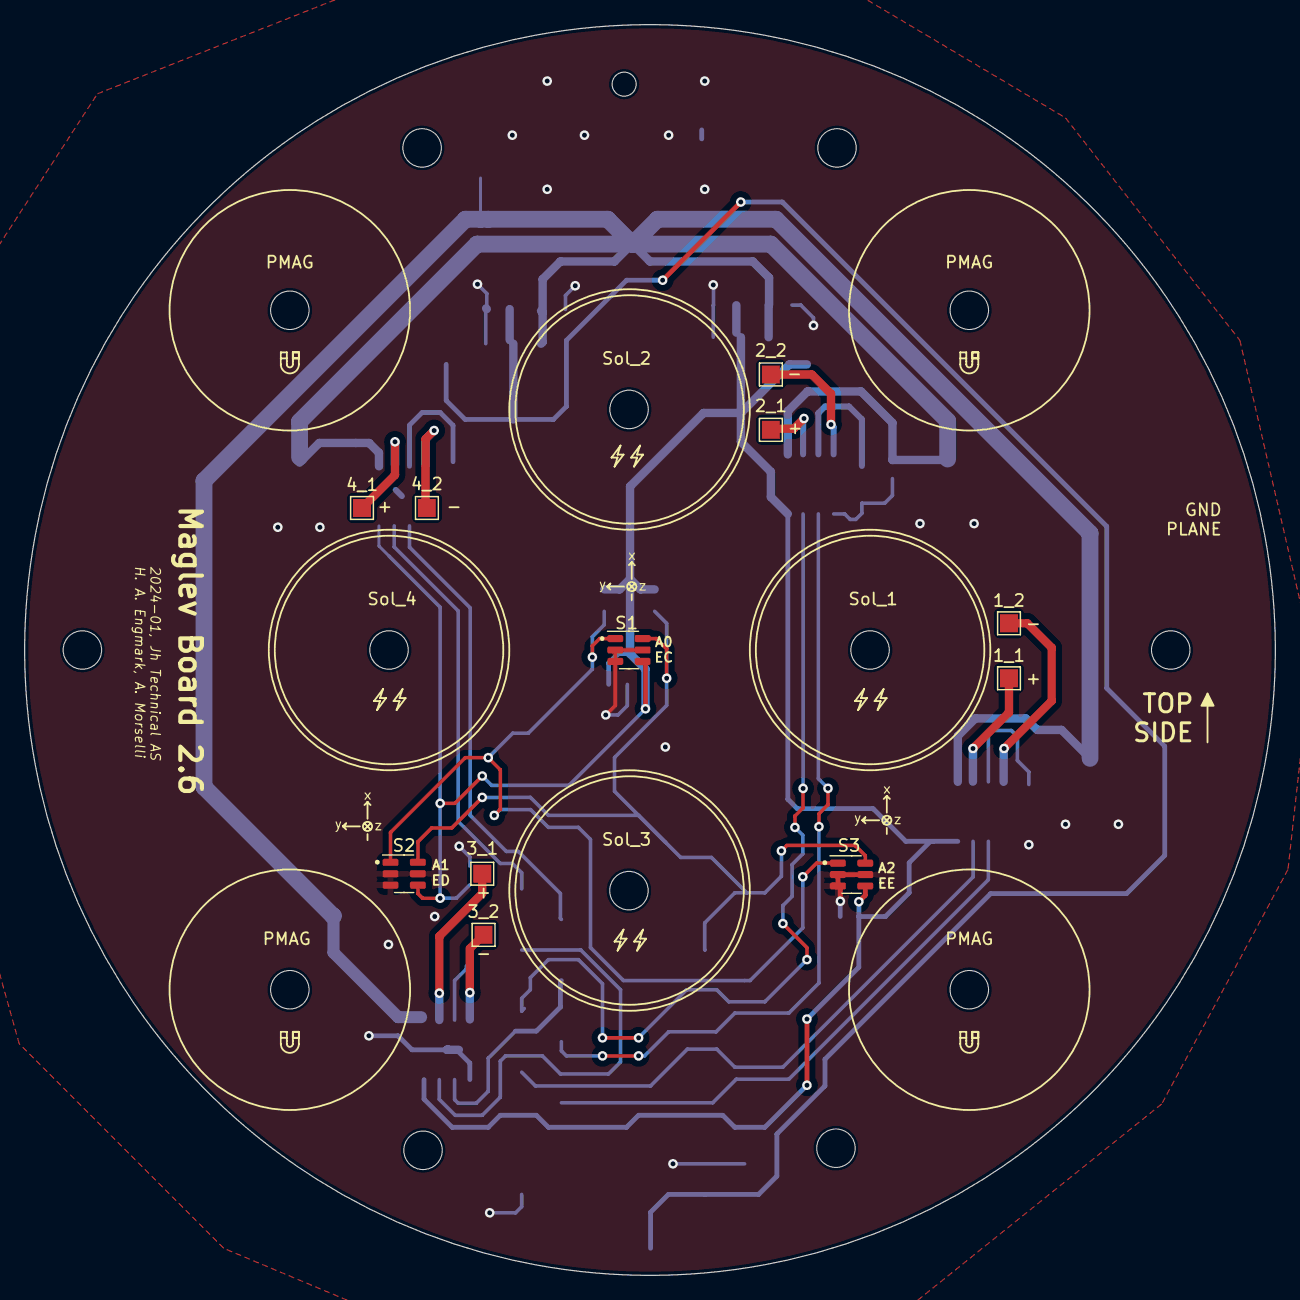
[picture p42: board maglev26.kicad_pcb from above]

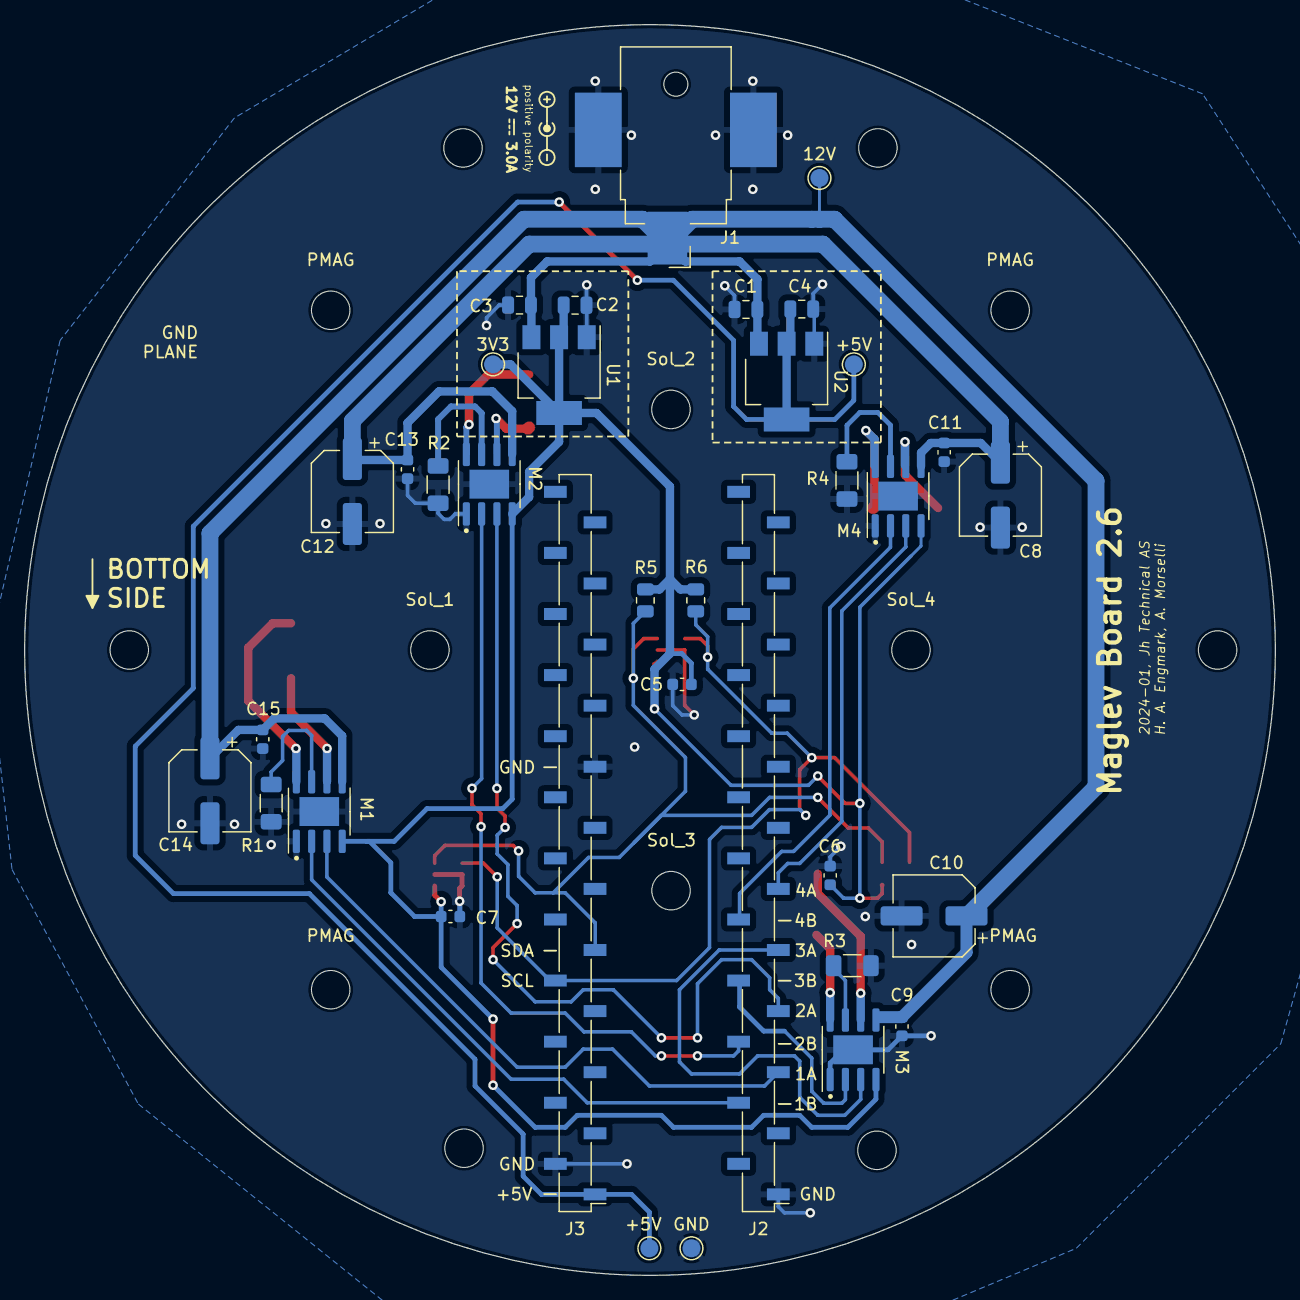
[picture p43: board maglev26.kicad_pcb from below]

Board: 2 copper layers, 104.0 x 104.0 mm, 59 parts (48 on the bottom side), 26 nets.

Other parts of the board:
3V3, 12V: TestPoint_Pad_D1.5mm
+5V, +5V#2: TestPoint_Pad_D1.5mm
GND: TestPoint_Pad_D1.5mm
PMAG: MountingHole_3.2mm_M3
PMAG#2, PMAG#3, PMAG#4, PMAG#5, PMAG#6: MountingHole_3.2mm_M3
REF2, REF3, REF4: MountingHole_3.2mm_M3
Sol_1, Sol_2, Sol_3, Sol_4: MountingHole_3.2mm_M3

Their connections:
+3.3V: 3V3.1; also elsewhere on the board
+5V: +5V.1, +5V#2.1; also elsewhere on the board
+12V: 12V.1; also elsewhere on the board
GND: GND.1; also elsewhere on the board

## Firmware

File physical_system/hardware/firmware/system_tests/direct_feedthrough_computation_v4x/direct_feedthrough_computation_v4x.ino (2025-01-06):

#include "TLx493D_inc.hpp"
#include <TCA9548.h>
#include <Wire.h>

// Sample timer
const double f_s = 5000; // Hz
const int T = round(1e6 / f_s);
unsigned long prev_time = 0;

// Use xensiv library namespace
using namespace ifx::tlx493d;

// Sensor initialization (use the same variant as in the first code)
TLx493D_A1B6 Sensor(Wire, TLx493D_IIC_ADDR_A0_e);

// Multiplexer initialization
TCA9548 mux_sensors(0x70);
#define RESET_I2C 26 // Define your reset pin number

// Motor driver pins setup
//// Motor driver 1
#define MD1_IN1 4
#define MD1_IN2 5

//// Motor driver 2
#define MD2_IN1 2
#define MD2_IN2 3

//// Motor driver 3
#define MD3_IN1 6
#define MD3_IN2 7

//// Motor driver 4
#define MD4_IN1 8
#define MD4_IN2 9

// Counters
int initCounter = 0;
unsigned long loopCounter = 0;

// Measurements
double bx = 0, by = 0, bz = 0;

// Mean of measurements
double meanBx = 0, meanBy = 0, meanBz = 0;

// Control variables for each solenoid
int u1 = 0, u2 = 0, u3 = 0, u4 = 0;

// Data collection for linear regression
const int data_size = 1000;
double u_data[data_size];
double B_data[data_size];
int data_index = 0;
int current_solenoid = 1;

void setup() {
  // Initialize serial
  Serial.begin(115200);
  Serial.println("Initialization...");

  // Set I2C frequency to 1MHz
  Wire.begin();
  Wire.setClock(1000000);

  // Reset Multiplexer to avoid issues during launch
  mux_sensors.setResetPin(RESET_I2C);
  mux_sensors.reset();
  if (mux_sensors.begin() == false) {
    Serial.println("COULD NOT CONNECT TO MULTIPLEXER");
  }

  // Enable and select the appropriate channel (same as first code)
  mux_sensors.enableChannel(7);
  mux_sensors.selectChannel(7);

  // Initialize sensor
  Sensor.begin();

  // Initialize motor drivers and set PWM resolution/frequency as in the first code
  analogWriteResolution(8);

  pinMode(MD1_IN1, OUTPUT);
  pinMode(MD1_IN2, OUTPUT);
  pinMode(MD2_IN1, OUTPUT);
  pinMode(MD2_IN2, OUTPUT);
  pinMode(MD3_IN1, OUTPUT);
  pinMode(MD3_IN2, OUTPUT);
  pinMode(MD4_IN1, OUTPUT);
  pinMode(MD4_IN2, OUTPUT);

  analogWriteFrequency(MD1_IN1, 32258);
  analogWriteFrequency(MD1_IN2, 32258);
  analogWriteFrequency(MD2_IN1, 32258);
  analogWriteFrequency(MD2_IN2, 32258);
  analogWriteFrequency(MD3_IN1, 32258);
  analogWriteFrequency(MD3_IN2, 32258);
  analogWriteFrequency(MD4_IN1, 32258);
  analogWriteFrequency(MD4_IN2, 32258);

  // Start with all solenoids off
  digitalWrite(MD1_IN1, LOW);
  digitalWrite(MD1_IN2, LOW);
  digitalWrite(MD2_IN1, LOW);
  digitalWrite(MD2_IN2, LOW);
  digitalWrite(MD3_IN1, LOW);
  digitalWrite(MD3_IN2, LOW);
  digitalWrite(MD4_IN1, LOW);
  digitalWrite(MD4_IN2, LOW);

  // Compute initial sensor mean for calibration (similar approach as first code)
  while (initCounter < 1000) {
    delay(1);  // Short delay between sensor readings
    double tempX = 0, tempY = 0, tempZ = 0;
    Sensor.getMagneticField(&tempX, &tempY, &tempZ);
    meanBx += tempX / 1000;
    meanBy += tempY / 1000;
    meanBz += tempZ / 1000;
    initCounter++;
  }
}

void linear_regression(double x[], double y[], int n, double &slope, double &intercept) {
  double sum_x = 0, sum_y = 0, sum_xy = 0, sum_xx = 0;
  for (int i = 0; i < n; i++) {
    sum_x += x[i];
    sum_y += y[i];
    sum_xy += x[i] * y[i];
    sum_xx += x[i] * x[i];
  }
  double denominator = n * sum_xx - sum_x * sum_x;
  if (denominator != 0) {
    slope = (n * sum_xy - sum_x * sum_y) / denominator;
    intercept = (sum_y - slope * sum_x) / n;
  } else {
    slope = 0;
    intercept = 0;
  }
}

int map_from_u_to_pwm(int u) {
  double a = (165.0 - 135.0)/255.0;
  double b = 135.0;

  if (u > 0) {
    return round(a*u + b); 
  } else {
    return round(a*u - b);
  }
}

void control_solenoid(int solenoid_num, int u) {
  int IN1, IN2;
  switch (solenoid_num) {
    case 1:
      IN1 = MD1_IN1;
      IN2 = MD1_IN2;
      break;
    case 2:
      IN1 = MD2_IN1;
      IN2 = MD2_IN2;
      break;
    case 3:
      IN1 = MD3_IN1;
      IN2 = MD3_IN2;
      break;
    case 4:
      IN1 = MD4_IN1;
      IN2 = MD4_IN2;
      break;
    default:
      return;
  }

  int pwm = map_from_u_to_pwm(u);
  if (u > 0) {
    analogWrite(IN1, 0);
    analogWrite(IN2, abs(pwm));
  } else {
    analogWrite(IN1, abs(pwm));
    analogWrite(IN2, 0);
  }
}

void loop() {
  unsigned long current_time = micros();
  if (current_time - prev_time >= T) {
    prev_time = current_time;

    // Get measurement (in mT), subtract mean offsets
    double tempX = 0, tempY = 0, tempZ = 0;
    if (!Sensor.getMagneticField(&tempX, &tempY, &tempZ)) {
      // If reading fails, print error
      Serial.println("ERROR : readRegisters failed !");
    }
    double rawBx = tempX - meanBx; 
    double rawBy = tempY - meanBy;
    double rawBz = tempZ - meanBz;

    bx = rawBx; 
    by = rawBy; 
    bz = rawBz;

    // Vary u from -255 to 255
    int u = loopCounter % 512;
    if (u <= 256) {
      u = -256 + u; // Increase from -255 to 0
    } else {
      u = u - 256; // Increase from 0 to 255
    }

    // Control current solenoid
    if (current_solenoid == 1) { // x positive
      control_solenoid(2, u);

      control_solenoid(1, 0);
      control_solenoid(3, 0);
      control_solenoid(4, 0);
    } else if (current_solenoid == 2) { // x negative
      control_solenoid(3, u);

      control_solenoid(1, 0);
      control_solenoid(2, 0);
      control_solenoid(4, 0);
    } else if (current_solenoid == 3) { // y positive
      control_solenoid(4, u);

      control_solenoid(1, 0);
      control_solenoid(2, 0);
      control_solenoid(3, 0);
    } else if (current_solenoid == 4) { // y negative
      control_solenoid(1, u);

      control_solenoid(2, 0);
      control_solenoid(3, 0);
      control_solenoid(4, 0);
    }

    // Record data for linear regression
    if (data_index < data_size) {
      u_data[data_index] = u;

      // Choose the magnetic field component affected by the current solenoid
      double b = 0;
      if (current_solenoid == 1 || current_solenoid == 2) {
        b = bx;
      } else {
        b = by;
      }

      B_data[data_index] = b;
      data_index++;

    } else {
      double slope, intercept;
      linear_regression(u_data, B_data, data_size, slope, intercept);

      Serial.print("Compensation Factor for Solenoid ");
      if (current_solenoid == 1) {
        Serial.print("x positive");
      } else if (current_solenoid == 2) {
        Serial.print("x negative");
      } else if (current_solenoid == 3) {
        Serial.print("y positive");
      } else if (current_solenoid == 4) {
        Serial.print("y negative");
      }

      Serial.print(": ");
      Serial.println(slope * 255);

      // Reset data index and move to next solenoid
      data_index = 0;
      current_solenoid++;
      if (current_solenoid > 4) {
        current_solenoid = 1; // Start over
        Serial.println("#############################################");
      }
    }

    loopCounter++;
  }
}

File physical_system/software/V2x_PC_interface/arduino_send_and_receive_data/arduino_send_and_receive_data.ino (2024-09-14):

#include <Tle493d_a2b6.h>
#include <Wire.h>

// ========================================================
//                      FUNCTION PROTOTYPES
// ========================================================
bool receiveSerialData(int16_t* receivedData);
void readSensorData(float* sensorValues);
void setSolenoidCurrents(const int16_t* receivedData);
void updateDataBuffer(const float* sensorValues, const int16_t* currentSolenoidCurrents);
void sendDataBuffer();
void analogWriteMotor(int pwm, int pin1, int pin2);
void resetSolenoidCurrents();

// ========================================================
//                      TIMING VARIABLES
// ========================================================
unsigned long lastSampleTime = 0;                // Tracks the last sample time
unsigned long sampleInterval = 200;              // Sampling interval in microseconds (5kHz sampling rate)
unsigned long lastDataReceivedTime = 0;          // Tracks the last time data was received

// ========================================================
//                    SENSOR CONFIGURATION
// ========================================================
Tle493d_a2b6 sensors[] = {
    Tle493d_a2b6(Tle493d::FASTMODE, Tle493d::TLE493D_A0),
    // Tle493d_a2b6(Tle493d::FASTMODE, Tle493d::TLE493D_A1),
    // Tle493d_a2b6(Tle493d::FASTMODE, Tle493d::TLE493D_A2)
};
constexpr int NUM_SENSORS = sizeof(sensors) / sizeof(sensors[0]);
constexpr int PWM_FREQUENCY = 20000;//32226.56;             // Frequency for PWM to avoid audible tones
constexpr int PWM_BIT_SIZE = 12;
constexpr int PWM_MAX = pow(2,PWM_BIT_SIZE);

// ========================================================
//                    SOLENOID CONFIGURATION
// ========================================================

// y-
constexpr int MD1_IN1 = 3;
constexpr int MD1_IN2 = 2;

// x+
constexpr int MD2_IN1 = 5;
constexpr int MD2_IN2 = 4;

// x-
constexpr int MD3_IN1 = 7;
constexpr int MD3_IN2 = 6;

// y+
constexpr int MD4_IN1 = 9;
constexpr int MD4_IN2 = 8;

constexpr int MOTOR_PINS[][2] = {
    {MD2_IN1, MD2_IN2}, // x+
    {MD3_IN1, MD3_IN2}, // x-
    {MD4_IN1, MD4_IN2}, // y+
    {MD1_IN1, MD1_IN2}, // y-
};
constexpr int NUM_MOTOR_PINS = sizeof(MOTOR_PINS) / sizeof(MOTOR_PINS[0]);

// ========================================================
//                  DATA RECEPTION SETUP
// ========================================================
const byte MAX_RECEIVE_BYTES = 2 * NUM_MOTOR_PINS; // Max bytes to receive, matches int16_t values count for solenoids
byte serialReceiveBuffer[MAX_RECEIVE_BYTES];       // Buffer to hold incoming serial data
static byte receiveBufferIndex = 0;                // Index for filling serialReceiveBuffer

// Serial communication state flags
bool isReceivingData = false;                      // Indicates if currently receiving data
bool isBufferReadyToSend = false;                  // Indicates when the data buffer is ready to send
bool solenoidsResetDueToTimeout = false;           // Indicates if solenoids have been reset due to timeout

// Serial communication markers
const char PACKET_START_MARKER = '<';              // Start marker for incoming data packets
const char PACKET_END_MARKER = '>';                // End marker for incoming data packets

byte incomingByte;                                 // Holds each incoming byte from Serial.read()
int16_t solenoidCurrents[NUM_MOTOR_PINS] = {0};    // Array to store received int16_t values for motor pins

// ========================================================
//                  DATA TRANSMISSION SETUP
// ========================================================

// Define byte sizes associated with specific data types
constexpr int BYTES_PER_TIMESTAMP = sizeof(unsigned long);         // 4 bytes for timestamp
constexpr int BYTES_PER_SENSOR_MEASUREMENT = sizeof(float);        // 4 bytes for each sensor measurement (float)
constexpr int BYTES_PER_SOLENOID_CURRENT = sizeof(int16_t);        // 2 bytes for each solenoid current (int16_t)

// Calculate the total bytes per sample
constexpr int BUFFER_SIZE = 5;                                     // Number of samples to accumulate before sending
constexpr int SAMPLES_PER_SENSOR = 3;                              // Three values per sensor (X, Y, Z)
constexpr int TOTAL_BYTES_PER_SAMPLE = BYTES_PER_TIMESTAMP + 
                                       (SAMPLES_PER_SENSOR * NUM_SENSORS * BYTES_PER_SENSOR_MEASUREMENT) + 
                                       (NUM_MOTOR_PINS * BYTES_PER_SOLENOID_CURRENT);

// Define the send buffer using the corrected size
byte serialSendBuffer[BUFFER_SIZE][TOTAL_BYTES_PER_SAMPLE];        // Buffer to store data for sending
int bufferIndex = 0;                                               // Index to keep track of buffer position

// ========================================================
//                       SETUP FUNCTION
// ========================================================
void setup() {
    Serial.begin(9600); // Initialize Serial (USB)

    // Initialize sensors
    for (int i = 0; i < NUM_SENSORS; i++) {
        sensors[i].begin();
    }

    // Modify I2C clock speed (IMPORTANT: HAS TO HAPPEN AFTER SENSOR INITIALIZATION!)
    Wire.begin();
    Wire.setClock(3400000);

    // Initialize motor drivers
    analogWriteResolution(PWM_BIT_SIZE);

    for (int i = 0; i < NUM_MOTOR_PINS; i++) {
        pinMode(MOTOR_PINS[i][0], OUTPUT);
        pinMode(MOTOR_PINS[i][1], OUTPUT);

        digitalWrite(MOTOR_PINS[i][0], LOW); // Start with motor drivers off
        digitalWrite(MOTOR_PINS[i][1], LOW);

        analogWriteFrequency(MOTOR_PINS[i][0], PWM_FREQUENCY); // Set PWM frequency
        analogWriteFrequency(MOTOR_PINS[i][1], PWM_FREQUENCY);
    }

    delay(2000); // Wait before starting main loop
}

// ========================================================
//                        MAIN LOOP
// ========================================================
void loop() {
    unsigned long currentTime = micros();

    // Check if it's time to sample data (5kHz)
    if (currentTime - lastSampleTime >= sampleInterval) {
        lastSampleTime = currentTime;

        int16_t receivedData[NUM_MOTOR_PINS];  // Array for received current values
        if (receiveSerialData(receivedData)) { // Receive data from Serial
            lastDataReceivedTime = millis();   // Update last data received time
            setSolenoidCurrents(receivedData); // Update solenoid currents first
            solenoidsResetDueToTimeout = false; // Reset timeout flag after receiving new data
        } else if (millis() - lastDataReceivedTime > 1000 && !solenoidsResetDueToTimeout) { // Check if more than 1 second has passed
            resetSolenoidCurrents();           // Reset solenoid currents to zero
            solenoidsResetDueToTimeout = true; // Set timeout flag to prevent repeated resets
        }

        float sensorValues[SAMPLES_PER_SENSOR * NUM_SENSORS]; // Array for sensor data
        readSensorData(sensorValues); // Read sensor values immediately after updating currents

        // Update the buffer with sensor values and the current state of the solenoids
        updateDataBuffer(sensorValues, solenoidCurrents); // Pass solenoidCurrents for accurate state capture

        if (isBufferReadyToSend) { // Check if the buffer is full
            sendDataBuffer(); // Send data if buffer is ready
        }
    }
}

// ========================================================
//                    FUNCTION DEFINITIONS
// ========================================================
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

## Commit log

2024-01-12 Added an Arduino script and libraries
2024-01-19 Adding PCB blueprints
    [maglev cv2-B_Cu.gbl, maglev cv2-B_Cu.gbr, maglev cv2-B_Mask.gbr, maglev cv2-B_Mask.gbs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]
2024-02-20 Adding blueprints
    [bom.csv, designators.csv, maglev26-B_Cu.gbl, maglev26-B_Mask.gbs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]
2024-04-09 Bugfix: Sensor measurements
    All other sensors besides the one in the origin did not measure the field of the levitating magnet correctly.
2024-09-07 Bug-fixing typecasting problems
    Premature typecasting in teensy script lead to division by zero in Matlab.
2024-09-14 Fixed issue with motor driver, cleaned up example
    Fixed motor driver issue by changing to "slow decay mode". Cleaned up example code to work with this change (added estimate of solenoid dynamics).
2025-01-06 Added design files for V4.0
    [BOM_maggy_V40.xlsx, Drill_NPTH_Through.DRL, Drill_PTH_Through.DRL, Drill_PTH_Through_Via.DRL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]
2025-01-06 Adding some sensor filtering examples
    PD control with different types of filters
2025-01-06 Added example teaching material
    Example assignment given in the course TTK4111 at NTNU in the fall of 2024.
2025-01-06 Reorganized files
    [Arduino_imp_calc_time.csv, Arduino_imp_controller_time.csv, Arduino_imp_total_comp_time.csv]
2025-01-21 Added results from Giuseppe
    [measured_rotation.csv, parameters_constant.csv, parameters_variable.csv]
2025-02-06 Fixed issues with TLE implementation
    Sensor has to be initialized before the clock is set
2025-02-07 Fixed example for V4 with TLV sensors
2025-02-07 Added blueprints for V4.1
    [BOM_Board1_PCB1_2025-02-07.xlsx, Drill_NPTH_Through.DRL, Drill_PTH_Through.DRL, Drill_PTH_Through_Via.DRL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]
2025-03-01 Added automatic feedthrough calibration
2025-03-07 Various updates to V4x PD Example
    Added:
    - Filtering on input
    - Anti sensor lock-up
    - Fixed reset on power-up
    - Better tuning
2025-03-28 Added README.md arduino setup guide
2025-04-04 Updated V4x example for robustness
    Added reading from multiple sensors, reorganized functions and files, added more robust sensor freeze recovery, added user friendly description at the head of the main file
